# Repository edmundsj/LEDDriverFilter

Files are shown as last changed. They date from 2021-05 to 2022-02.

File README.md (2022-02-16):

# LED Driver LC Filter

Filtering can provide shot-noise-limited performance from noisy drive electronics when driving LEDs with fixed currents. This LC filter is designed to aggressively lowpass filter an input current to a thorlabs LED to achieve shot-noise-limited output currents.

## Features
- Dual LC filter
- 1Hz -3dB frequency
- Shot-noise-limited performance at 1A drive current above 6Hz
- 1.3A maximum DC current (inductor-limited)
- Optional 0805 sense resistors at input and output
- Input screw terminal for connectorization to male M8-4 connector
- Output M8-4 female connector for connectorization to thorlabs LEDs
- Kicad schematic/PCB files, fabrication gerbers

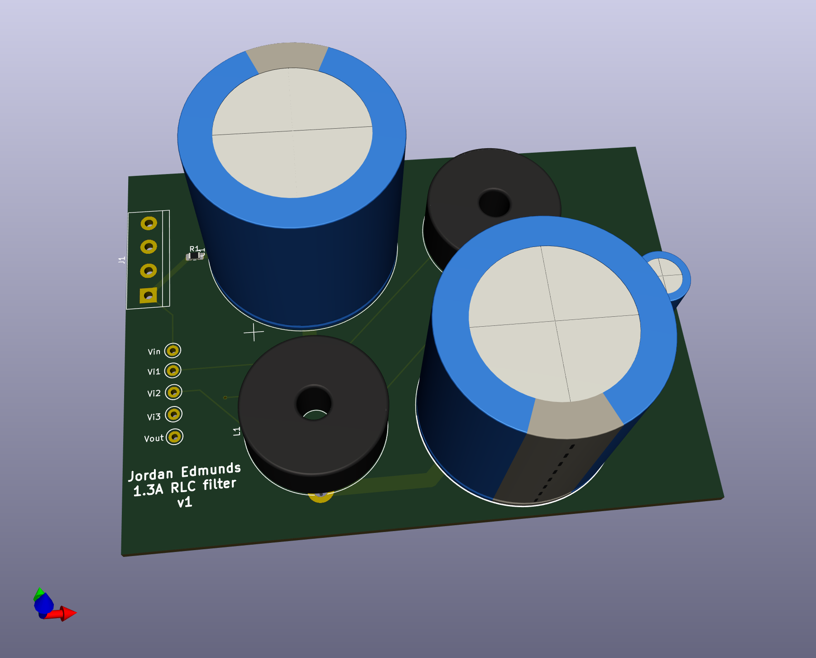
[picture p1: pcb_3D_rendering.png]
PCB 3D view

Fig 0. 3D kicad rendering of PCB

[Fabricated PCB]
Fig 1. Image of fabricated PCB

## Simulations
Simulations were done in LTSpice using manufacturer specified parasitic values for the series resistance of capacitors (10mOhm) and inductors (1.27Ohm). 10mOhm sense resistor values were used.

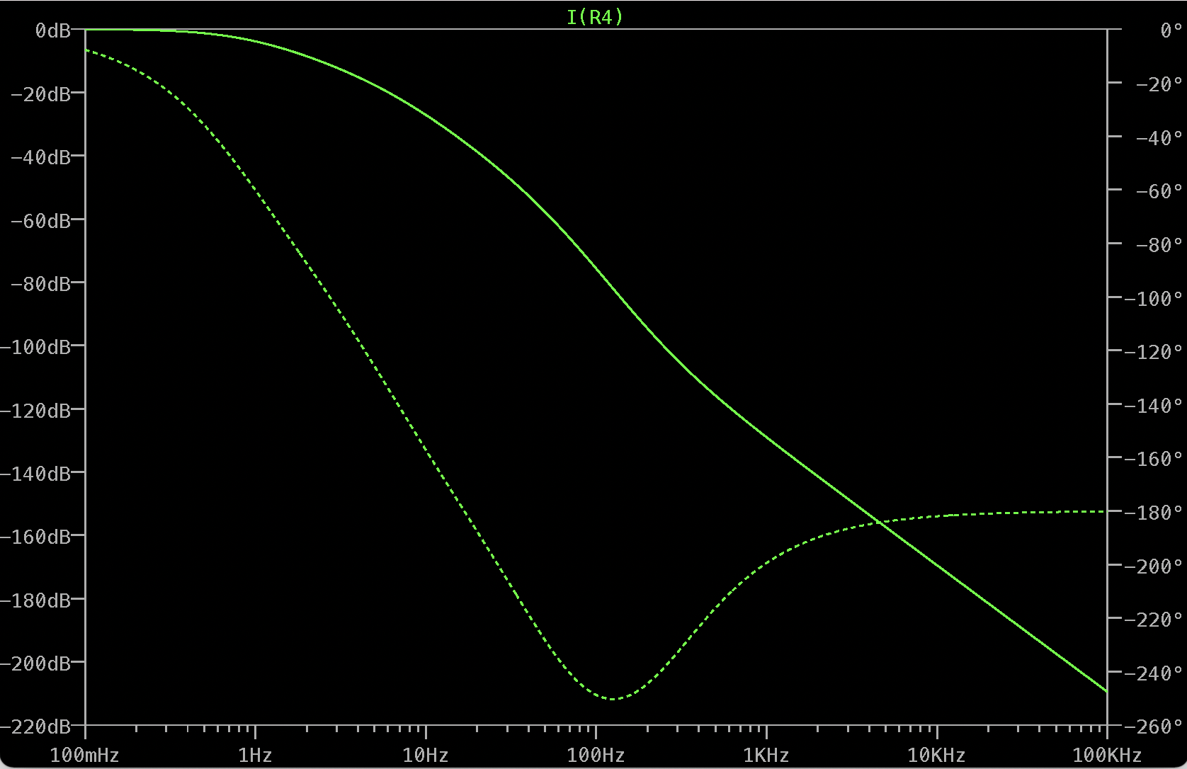
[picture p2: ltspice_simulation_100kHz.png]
100kHz simulation

Fig 2. Filter response from 0.1Hz - 100kHz

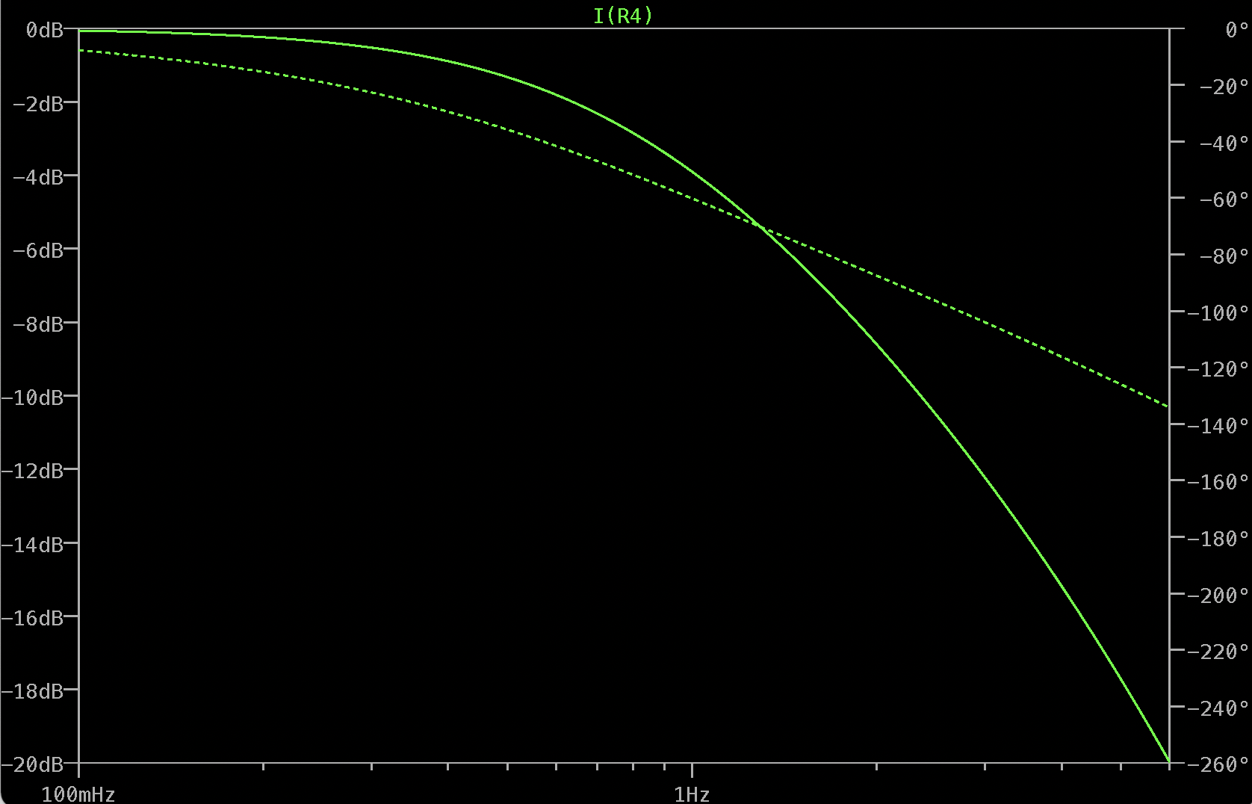
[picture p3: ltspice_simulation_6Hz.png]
6Hz simulation zoomed

Fig 3. Filter response from 0.1Hz - 6Hz (first 20dB of rolloff). Note the -3dB frequency is approximately 1Hz.

## Test Data
Initial tests indicate the Thorlabs LEDD1B has current noise >20dB in excess of the shot noise limit when driving LEDs at 1A.

[TO BE ADDED]
Fig 4. Measured transfer function of LCR filter from 0.1Hz - 10kHz

[TO BE ADDED]
Fig 5. Measured noise spectra without filter

[TO BE ADDED]
Fig 6. Measured noise spectra with filter in series

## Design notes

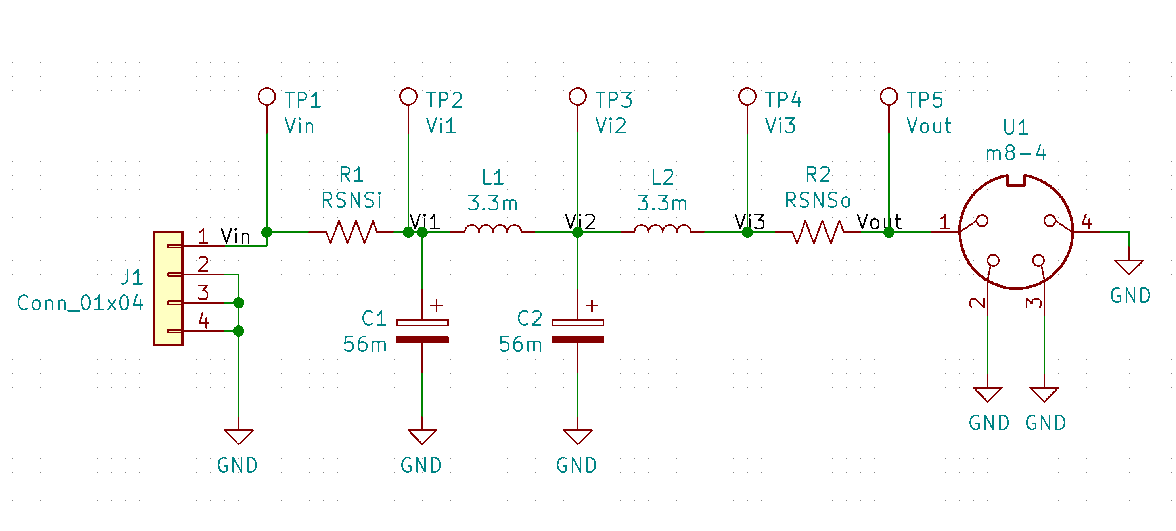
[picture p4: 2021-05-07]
LCR_filter_schematic.png

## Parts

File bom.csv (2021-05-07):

Reference | Value | Kind | Quantity | Manufacturer #
C1, C2 | 56m | Capacitor | 2 | SLPX563M016H4P3
J1 | None | Screw Terminal | 1 | TB007-508-04BE
L1, L2 | 3.3m | Inductor | 2 | AIRD-03-332K
R1, R2 | 10m | Resistor | 1 | None
TP1-5 | None | Test Point | 1 | None
U1 | None | M8 Female Connector | 1 | T4043014041-000
None | None | M8 Male Cable | 1 | T4061120004-001

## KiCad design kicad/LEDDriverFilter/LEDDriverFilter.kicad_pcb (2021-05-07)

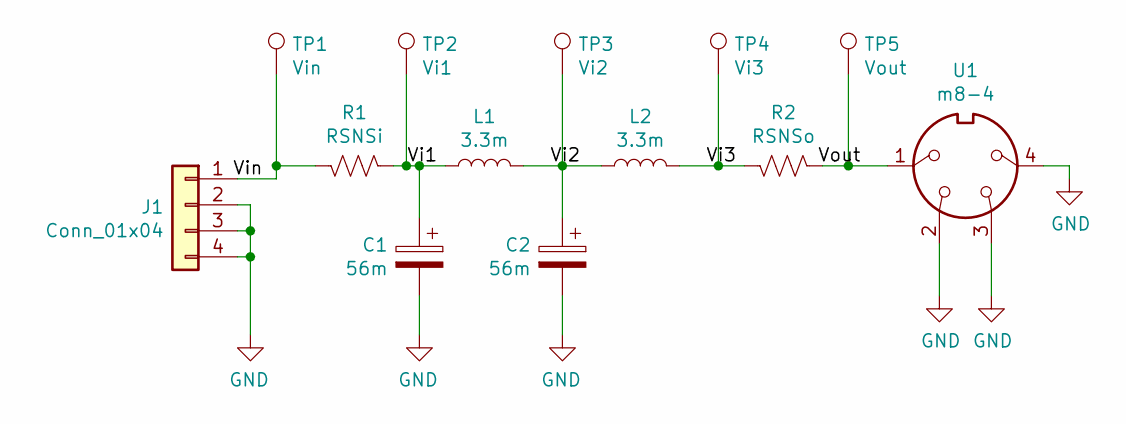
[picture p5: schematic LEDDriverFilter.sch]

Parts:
C1, C2: 56m; CP_Radial_D35.0mm_P10.00mm_SnapIn
J1: Conn_01x04; TerminalBlock_bornier-4_P5.08mm
L1, L2: 3.3m; L_Radial_D24.4mm_P22.90mm_muRATA_1400series
R1: RSNSi; R_0805_2012Metric_Pad1.15x1.40mm_HandSolder
R2: RSNSo; R_0805_2012Metric_Pad1.15x1.40mm_HandSolder
TP1: Vin; TestPoint_Keystone_5000-5004_Miniature
TP2: Vi1; TestPoint_Keystone_5000-5004_Miniature
TP3: Vi2; TestPoint_Keystone_5000-5004_Miniature
TP4: Vi3; TestPoint_Keystone_5000-5004_Miniature
TP5: Vout; TestPoint_Keystone_5000-5004_Miniature
U1: m8-4; M8_4POS

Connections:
/Vi1: C1.1, L1.2, R1.2, TP2.1
/Vi2: C2.1, L1.1, L2.2, TP3.1
/Vi3: L2.1, R2.1, TP4.1
/Vin: J1.1, R1.1, TP1.1
/Vout: R2.2, TP5.1, U1.1
GND: C1.2, C2.2, J1.2, J1.3, J1.4, U1.2, U1.3, U1.4

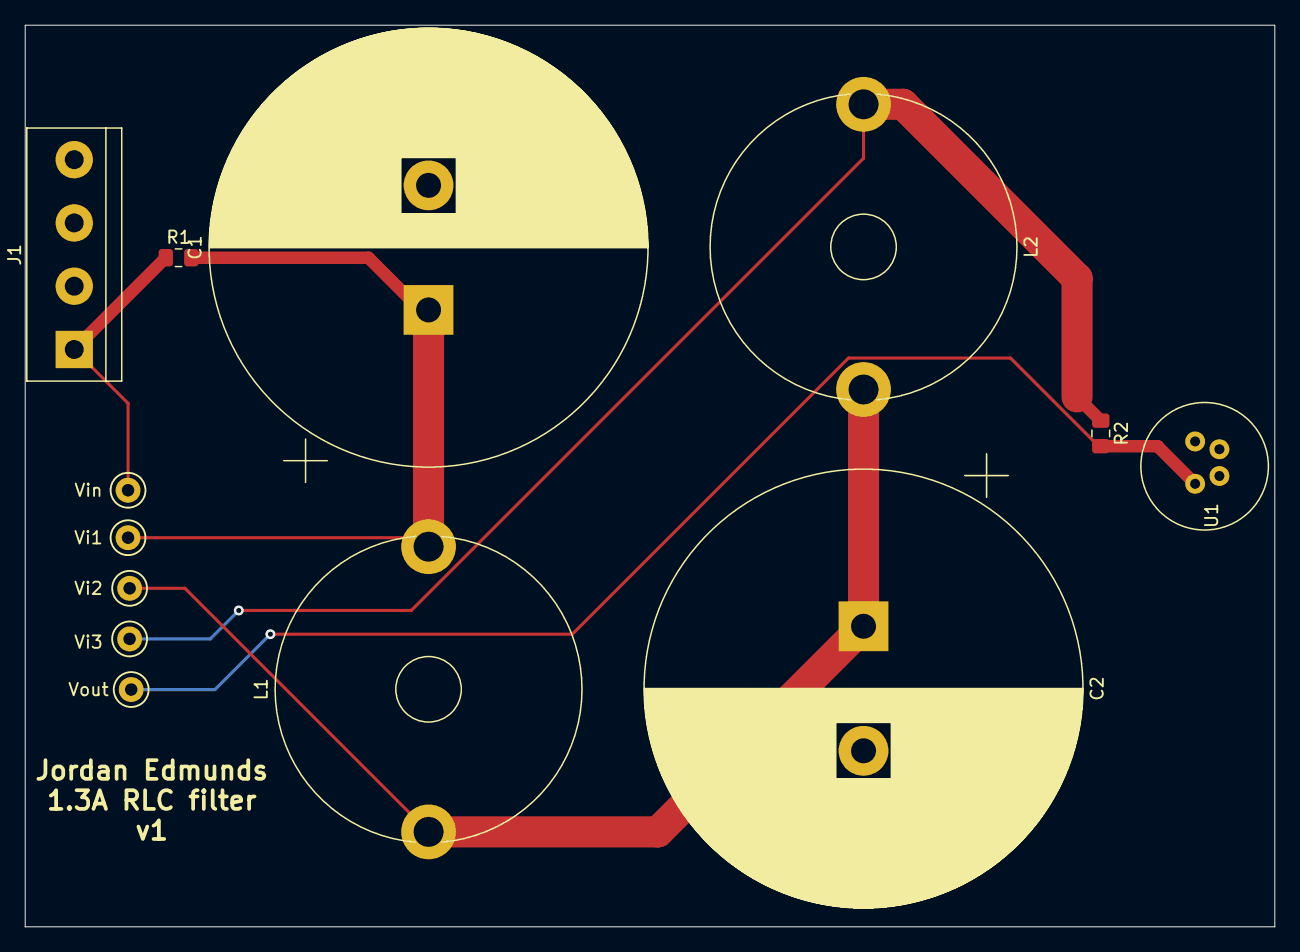
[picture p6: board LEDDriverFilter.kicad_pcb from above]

Board: 2 copper layers, 100.3 x 72.4 mm, 13 parts (0 on the bottom side), 6 nets.
